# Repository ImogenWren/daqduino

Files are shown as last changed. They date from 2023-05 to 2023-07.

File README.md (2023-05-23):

# DAQduino
 DAQ Arduino, Voltage and Current Data Aquisition Unit.
 
 ## Goal 
 DAQduino is a standalone DAQ device capable of logging data from 
a few sources to a CSV file on an SD card, sending data in realtime
to a PC, and displaying the data for a particular sensor on a screen
 
 ## Using Arduino for Data Aquisition
 
 _There are several different methods that could be used for basic Data Aquisition tasks with just a few sensors that are easy to integrate with the Arduino Platform._
 
 1. Arduino streams serial data in CSV format. 
    - Use Putty/Kitty to record log
    - Python program to log to file
    - LabVIEW program to log to file

 2. Arduino streams data in JSON format.
    - Use Putty/Kitty and export data later
    - Python to log to file

3. Arduino waits for serial message to release data packet
    - Putty/Kitty to record log
    - LabVIEW for full DAQ implementation
    - Python for basic IO Interface - command line?
    - Python Desktop App

4. Full Integration between arduino and desktop software.

### Functions:
 - 10v, 12v and 24v outputs for sensor power
 - 0 - 10v analog input
 - 0 - 5v TTL IO
 - 4 - 20mA input
 - OLED Screen
 - Encoder Control
 - Basic Scaling

#### Stretch Goals:
 - 0 - 10 v output
 - 0 - 20 mA output

### Communications:
- Serial Data
- Labveiw Integration?

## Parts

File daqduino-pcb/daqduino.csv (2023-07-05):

# | Reference | Qty | Value | Footprint | DNP | JLCpart | RSpart | FarnellPart | supplier | Cost
1 | C1 | 1 | 470n | Capacitor_SMD:C_0805_2012Metric_Pad1.18x1.45mm_HandSolder
2 | C2, C3, C4 | 3 | 100n | 000_Capacitors_Immo:C_0805_2012_HandSolder_kawaii |  | C779975 |  |  |  | 0.02
3 | D1 | 1 | red | Diode_SMD:D_0805_2012Metric_Pad1.15x1.40mm_HandSolder
4 | D2 | 1 | yellow | Diode_SMD:D_0805_2012Metric_Pad1.15x1.40mm_HandSolder
5 | D3 | 1 | green | Diode_SMD:D_0805_2012Metric_Pad1.15x1.40mm_HandSolder
6 | D4 | 1 | blue | Diode_SMD:D_0805_2012Metric_Pad1.15x1.40mm_HandSolder
7 | EC1, EC2 | 2 | 100u | Capacitor_SMD:CP_Elec_10x10
8 | J1 | 1 | 24v Power Input | 000_Connectors_Immo:TerminalBlock_Altech_AK300-2_P5.00mm
9 | J2 | 1 | Sense Current TestPoint | 000_Connectors_Immo:TerminalBlock_Altech_AK300-2_P5.00mm
10 | J3 | 1 | Bias Voltage & Resistor Selection | 000_Pin_Headers_Immo:PinHeader_2x03_P2.54mm-alt-pin-no
11 | J4 | 1 | Sensor Voltage Selection | 000_Pin_Headers_Immo:PinHeader_2x03_P2.54mm-alt-pin-no
12 | J5 | 1 | 2 Wire Sensor (4-20mA) | 000_Connectors_Immo:TerminalBlock_Altech_AK300-2_P5.00mm
13 | J7 | 1 | Micro_SD_Card-molex | 000_Connectors_Immo:microSD_HC_Molex_104031-0811 |  |  |  | 2678573 | https://uk.farnell.com/molex/104031-0811/connector-micro-sd-8pos/dp/2678573
14 | R1 | 1 | 220r | Resistor_SMD:R_0805_2012Metric_Pad1.20x1.40mm_HandSolder
15 | R2, R3, R10 | 3 | 10k | Resistor_SMD:R_0805_2012Metric_Pad1.20x1.40mm_HandSolder |  | C2930231 |  |  |  | 0.002
16 | R4 | 1 | 100r | Resistor_SMD:R_0805_2012Metric_Pad1.20x1.40mm_HandSolder |  | C217766 |  |  |  | 0.0093
17 | R5, R6, R7, R8, R9 | 5 | 3k3 | Resistor_SMD:R_0805_2012Metric_Pad1.20x1.40mm_HandSolder
18 | R11 | 1 | 4k7 | Resistor_SMD:R_0805_2012Metric_Pad1.20x1.40mm_HandSolder |  | C2930231 |  |  |  | 0.002
19 | R12 | 1 | 2k2 | Resistor_SMD:R_0805_2012Metric_Pad1.20x1.40mm_HandSolder |  | C2930231 |  |  |  | 0.002
20 | R13 | 1 | 1k | Resistor_SMD:R_0805_2012Metric_Pad1.20x1.40mm_HandSolder |  | C2930231 |  |  |  | 0.002
21 | TP1 | 1 | 24v TestPoint | TestPoint:TestPoint_Bridge_Pitch2.54mm_Drill1.0mm
22 | TP2 | 1 | 12v TestPoint | TestPoint:TestPoint_Bridge_Pitch2.54mm_Drill1.0mm
23 | TP3 | 1 | 5v TestPoint | TestPoint:TestPoint_Bridge_Pitch2.54mm_Drill1.0mm
24 | TP4 | 1 | 3v3 TestPoint | TestPoint:TestPoint_Bridge_Pitch2.54mm_Drill1.0mm
25 | TP5 | 1 | Bias TestPoint | TestPoint:TestPoint_Bridge_Pitch2.54mm_Drill1.0mm
26 | TP6 | 1 | Sense Voltage TestPoint | TestPoint:TestPoint_Bridge_Pitch2.54mm_Drill1.0mm
27 | U1 | 1 | LM358 | Package_SO:SOIC-8_3.9x4.9mm_P1.27mm |  |  | 689-6719 |  | https://uk.rs-online.com/web/p/op-amps/6896719?gb=s
28 | U2 | 1 | L7812 | Package_TO_SOT_THT:TO-220-3_Vertical |  |  | 793-1355 |  | https://uk.rs-online.com/web/p/voltage-regulators/7931355?gb=s
29 | U3 | 1 | TXS0108EPW | Package_SO:TSSOP-20_4.4x6.5mm_P0.65mm |  |  | 709-4639 |  | https://uk.rs-online.com/web/p/translator-ics/7094639?gb=s
30 | XA1 | 1 | Arduino_Uno_R3_Shield | PCM_arduino-library:Arduino_Uno_R3_Shield |  |  | 769-7409 |  | https://uk.rs-online.com/web/p/arduino/7697409?gb=s

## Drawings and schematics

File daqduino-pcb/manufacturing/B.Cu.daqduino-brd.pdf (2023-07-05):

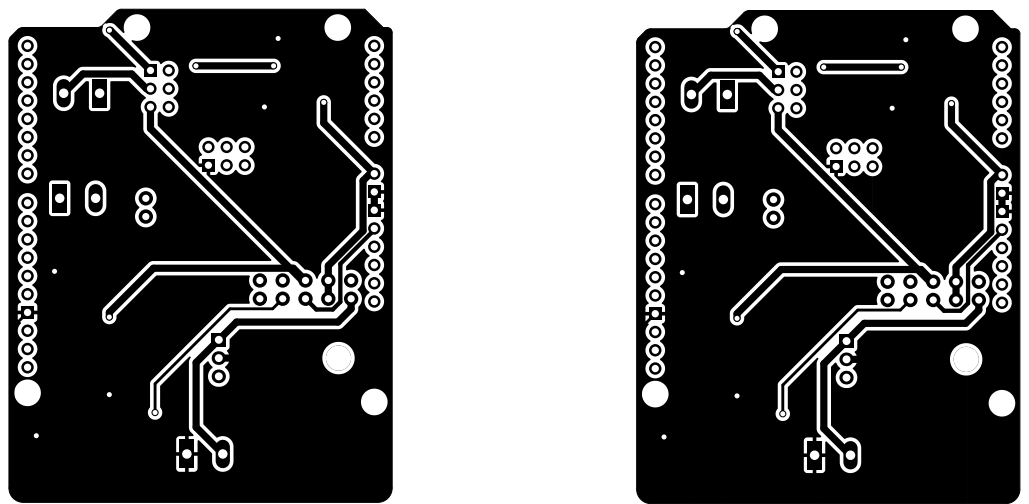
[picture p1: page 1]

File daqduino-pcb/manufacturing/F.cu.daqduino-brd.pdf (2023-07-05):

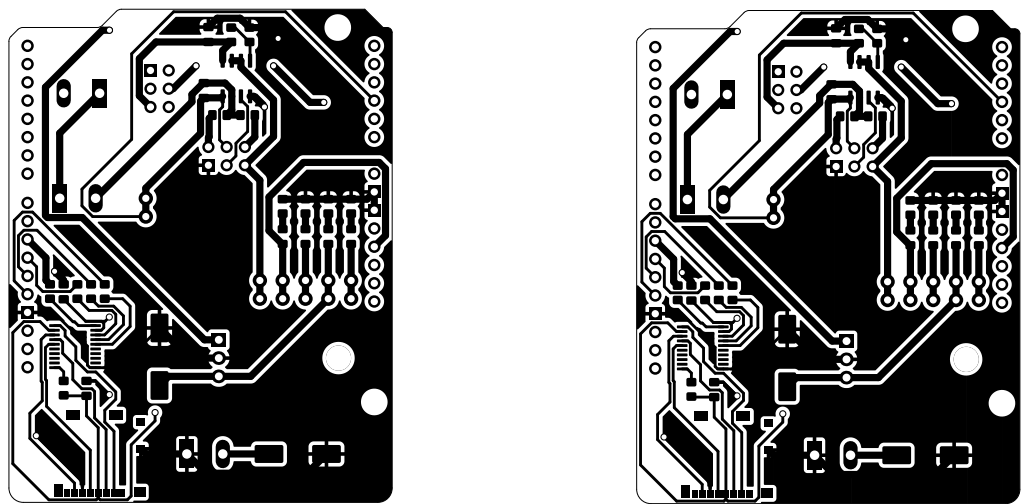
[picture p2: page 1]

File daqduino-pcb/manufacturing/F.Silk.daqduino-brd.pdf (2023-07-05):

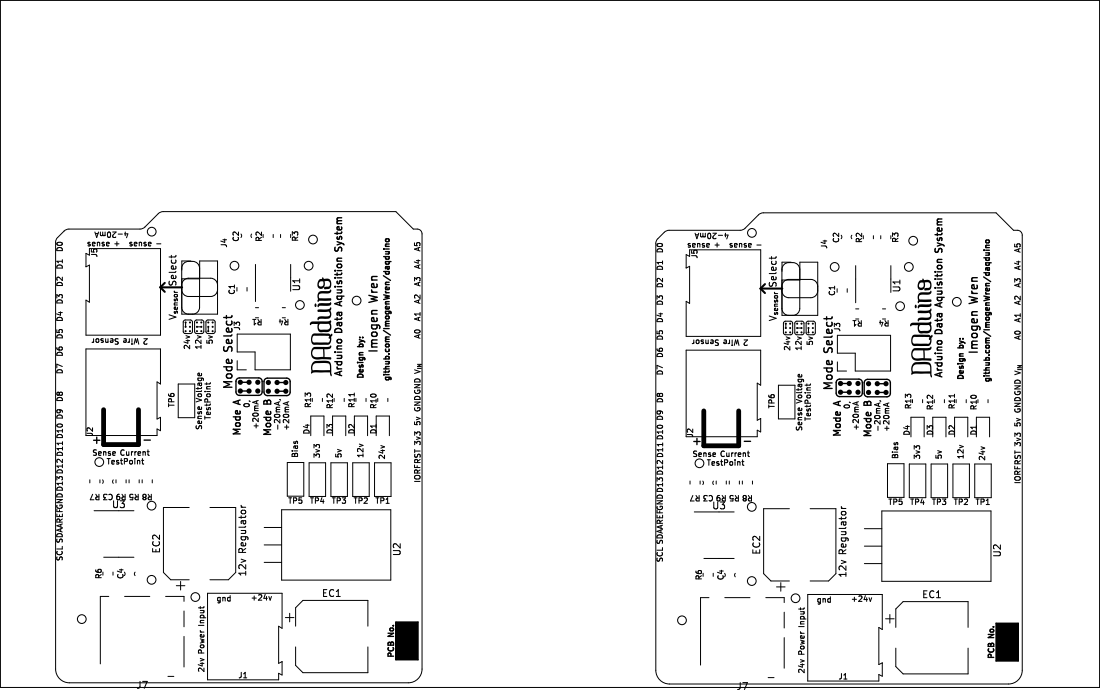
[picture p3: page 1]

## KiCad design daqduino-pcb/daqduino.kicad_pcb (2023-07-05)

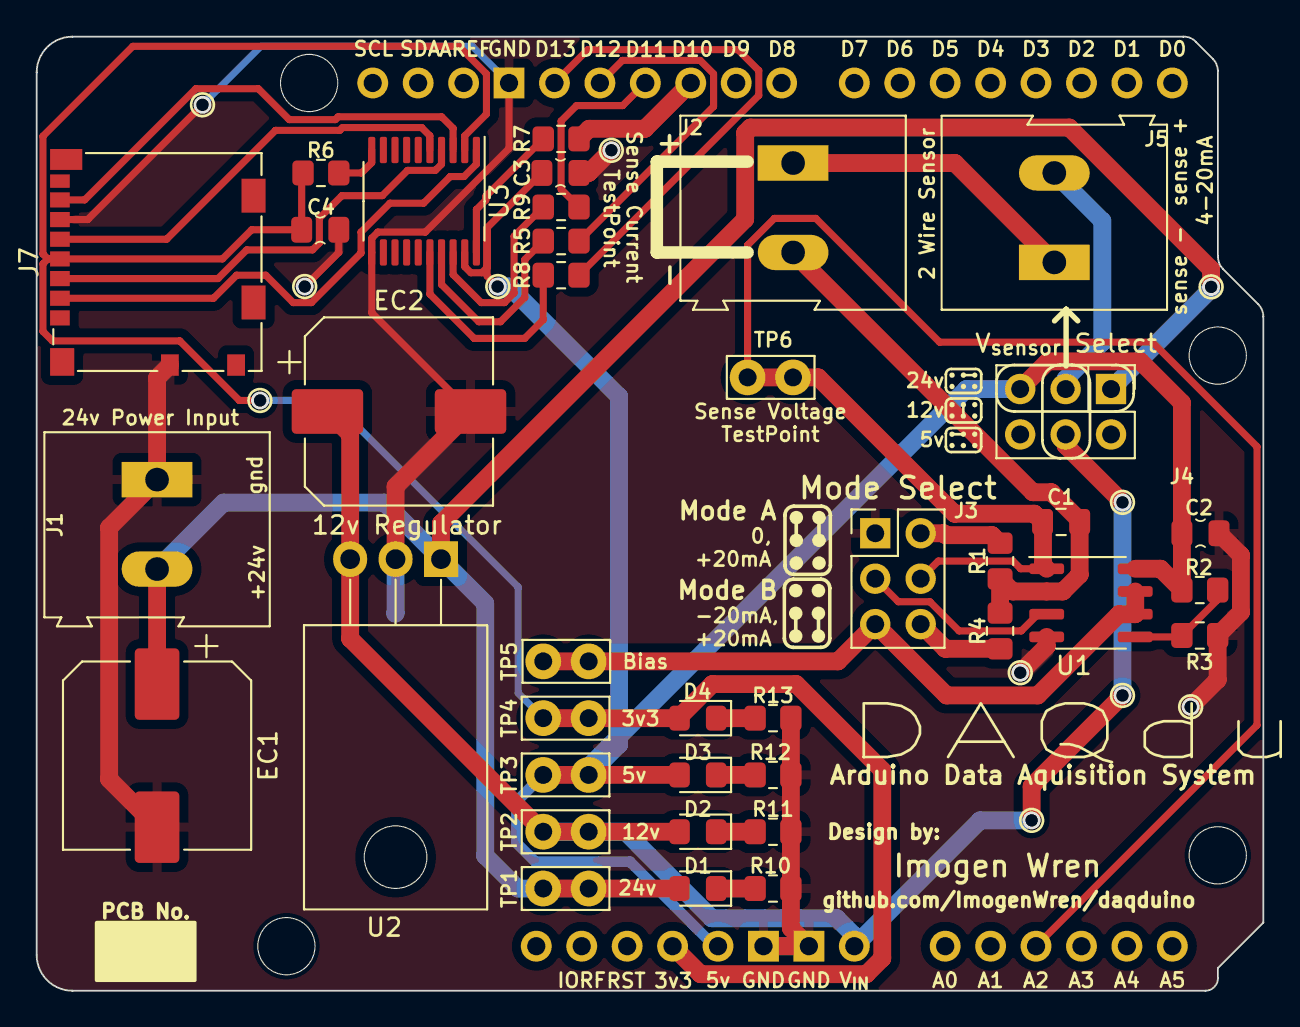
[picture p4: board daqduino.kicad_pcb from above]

Board: 2 copper layers, 68.6 x 53.3 mm, 39 parts (0 on the bottom side), 31 nets.

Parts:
C1: 470n; C_0805_2012Metric_Pad1.18x1.45mm_HandSolder
C2, C3, C4: 100n; C_0805_2012_HandSolder_kawaii
D1: red; D_0805_2012Metric_Pad1.15x1.40mm_HandSolder
D2: yellow; D_0805_2012Metric_Pad1.15x1.40mm_HandSolder
D3: green; D_0805_2012Metric_Pad1.15x1.40mm_HandSolder
D4: blue; D_0805_2012Metric_Pad1.15x1.40mm_HandSolder
EC1, EC2: 100u; CP_Elec_10x10
J1: 24v Power Input; TerminalBlock_Altech_AK300-2_P5.00mm
J2: Sense Current; TerminalBlock_Altech_AK300-2_P5.00mm
J3: Mode Select; PinHeader_2x03_P2.54mm-alt-pin-no
J4: V_{sensor} Select; PinHeader_2x03_P2.54mm-alt-pin-no
J5: 2 Wire Sensor; TerminalBlock_Altech_AK300-2_P5.00mm
J7: Micro SD Card; microSD_HC_Molex_104031-0811
R1: 220r; R_0805_2012Metric_Pad1.20x1.40mm_HandSolder
R2, R3, R10: 10k; R_0805_2012Metric_Pad1.20x1.40mm_HandSolder
R4: 100r; R_0805_2012Metric_Pad1.20x1.40mm_HandSolder
R5, R6, R7, R8, R9: 3k3; R_0805_2012Metric_Pad1.20x1.40mm_HandSolder
R11: 4k7; R_0805_2012Metric_Pad1.20x1.40mm_HandSolder
R12: 2k2; R_0805_2012Metric_Pad1.20x1.40mm_HandSolder
R13: 1k; R_0805_2012Metric_Pad1.20x1.40mm_HandSolder
TP1: 24v; TestPoint_Bridge_Pitch2.54mm_Drill1.0mm
TP2: 12v; TestPoint_Bridge_Pitch2.54mm_Drill1.0mm
TP3: 5v; TestPoint_Bridge_Pitch2.54mm_Drill1.0mm
TP4: 3v3; TestPoint_Bridge_Pitch2.54mm_Drill1.0mm
TP5: Bias; TestPoint_Bridge_Pitch2.54mm_Drill1.0mm
TP6: Sense Voltage; TestPoint_Bridge_Pitch2.54mm_Drill1.0mm
U1: LM358; SOIC-8_3.9x4.9mm_P1.27mm
U2: 12v Regulator; TO-220-3_Horizontal_TabDown
U3: TXS0108EPW; TSSOP-20_4.4x6.5mm_P0.65mm
XA1: Arduino_Uno_R3_Shield-simple

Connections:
/3V3_BUS: C4.1, D4.2 (A), J7.4 (VDD), R6.2, TP4.1, U3.2 (VCCA), XA1.3V3 (3.3V)
/5V_BUS: C2.1, C3.1, D3.2 (A), J4.3, R2.2, TP3.1, U1.8 (V+), U3.19 (VCCB), XA1.5V1 (5V)
/12V_BUS: D2.2 (A), EC2.1, J4.5, TP2.1, U2.3 (OUT), XA1.VIN
/24V_BUS: D1.2 (A), EC1.1, J1.2, J4.1, TP1.1, U2.1 (IN)
/BIAS_VOLTAGE: J3.2, U1.3 (+)
/CHIP_SELECT: R7.1, XA1.D10 (D10_CS)
/CLK: J7.5 (CLK), U3.5 (A4)
/CS: J7.2 (DAT3/CD), U3.1 (A1)
/D_{IN}: J7.3 (CMD), U3.4 (A3)
/D_{OUT}: J7.7 (DAT0), U3.3 (A2)
/MISO: R9.1, XA1.D11
/MOSI: R5.1, XA1.D12
/R_SET_A: C1.1, J2.2, R1.2, R4.2, U1.2 (-)
/R_SET_B: C1.2, J3.5, TP6.1, U1.1, XA1.A2
/SCK: R8.1, XA1.D13
/SENSE_CURRENT: J2.1, J5.1
/SENSOR_POWER: J4.2, J5.2
GND: C2.2, C3.2, C4.2, EC1.2, EC2.2, J1.1, J3.1, J7.6 (VSS), J7.9 (SHIELD), R3.1, R10.1, R11.1, R12.1, R13.1, U1.4 (V-), U2.2 (GND), U3.11 (GND), XA1.GND1 (GND), XA1.GND2 (GND), XA1.GND3 (GND)
unnamed: D1.1 (K), R10.2
unnamed: D2.1 (K), R11.2
unnamed: D3.1 (K), R12.2
unnamed: D4.1 (K), R13.2
unnamed: J3.3, TP5.1, U1.6 (-), U1.7
unnamed: J3.4, R4.1
unnamed: J3.6, R1.1
unnamed: R2.1, R3.2, U1.5 (+)
unnamed: R7.2, U3.20 (B1)
unnamed: R9.2, U3.18 (B2)
unnamed: R5.2, U3.17 (B3)
unnamed: R8.2, U3.16 (B4)
unnamed: R6.1, U3.10 (OE)

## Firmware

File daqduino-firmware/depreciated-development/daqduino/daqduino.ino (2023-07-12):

/*   DAQduino - Firmware - V0.1

          DAQduino is an open-source Data AQuisition (DAQ) Device
            designed to free researchers and students from
            the Tyranny of National Instruments and LabVIEW.

            It can be used as a standalone datalogger, saving data to an SD card for later,
            or it can be interfaced with a veriety of software to gather real-time data and 
            share this with other devices 

    This is Firmware Version 0.1. It will have reduced functionality while the system is being developed.

    Version 0.1
    Imogen Wren H.
    05/07/2023

*/


/*  Initial Scaling - Based on "theory" and "maths"

          Volts per ADC = 4.89 mV
                        = 0.00489 V

          DAQduino internal amplifier is set up for 

          20 mA ~= 4.4 V output

          Therefore:

          scale:

          mA = 20/4.4(Vmeasured)
          mA = 4.54(Vmeasured)
*/

/*  First Test

          To account for DC offset in readings, measure difference between multimeter readings and DAQduino reporting.
          To Start: 
|         | ADC   |  Vreported  | Vmeasured  | Vdiff    | % diff   | mA reported | mA measured  | mA diff |
|---      |---    |---          |---         |---       |---       |---          |---           |---      |
| Lowest  | 162   |   0.792     |   0.772    |  0.02    |          | 3.596       | 2.11         | 1.486   |
|MidRange | 400   |   1.956     |   1.888    |  0.068   |          | 8.880       | 20.69        |-11.81   |  
| Highest | 632   |   3.090     |   2.977    |  0.113   |          | 14.031      | 23.47        |-9.439   |
|---      |---    |---          |---         |---       |---       |---          |---           |         |


*/

/* Actual Scale - Defintion Based on Measurements

    - This method of calibration should work for any sensor with a linear output, as long as measured voltage is accurate, and the true value used in calibration is known
          - e.g. if a pressor sensor voltage can be tested at a specific known pressure.

Step 1: Record the detected voltage and the sensor true value for minimum and maximum possible datapoints.
Step 2: Calculate range, divisions and offset for each set of data.
Step 3: Place Values into algorithm as indicated
Step 4: ...?? Profit ?

    - Use the following table to assist

|                        | Voltage (V)  |Sensor True Value (measured)|       |
|---                     |---           |---                         |---    |
|Min                     |	 3.295      |	     2.06	                 |  mA	 |
|Max                     |  4.298	      |    	22.4	                 |  mA   |	
|Range (max - min)       |	 1.003      |     20.34                  |  mA   |
|ScaleFactor(Voltage/STV)|	 0.049		  |	     1.0                   | V/mA  |
|ScaleFactor(STV/Voltage)|	 1.0		    |     20.3                   | mA/v  |
|Offset                  |  3.295       |	     2.06                  |  mA   |	       	
					
      sensor_value = ((Vin - Voffset) * ScaleFactor(mA/V)) + mAoffset 			

*/

//#define ADC_VOLTS_SCALER 0.0048876  // Value Gained via maths for ADC scale calculation
//#define ADC_VOLTS_SCALER 0.0047341     // Value taking into account 3.14% average difference between top and bottom values
//#define ADC_VOLTS_SCALER 0.0045854     // wwinging it at this point (too low)
//#define ADC_VOLTS_SCALER 0.0046969       // still slightly too low
#define ADC_VOLTS_SCALER 0.0047339

#define mA_PER_VOLT 20.3
#define mA_OFFSET 2.06
#define V_OFFSET 3.295

/* Algorithm:

mA = (Vreading - V_OFFSET)* mA_PER_VOLT + mA_OFFSET

*/
#define VOLTAGE_SENSE_PIN A2
#define SD_SELECT_PIN 10


#define BENCHMARK_SAMPLING  // print benchmark testing output for sampling function
//#define BENCHMARK_LOOP      // print benchmark testing output for entire program loop  // use to check sample rate targets met
//#define PRINT_RAW_DATA     // Print all raw ADC samples before averaging (for debugging purposes)
#define SERIAL_PRINT_TRUE  // Print data output to serial monitor (comment out for faster sampling)?
#define LOG_TO_SD_CARD     // Log data to SD card

//#define USE_SDFAT_LIB  // User option to use SD FAT library instead of standard one (untested)
// If undefined then typical arduino library is used.

#include "sd-functions.h"


bool cardAvailable = false;  // must start true then will be made false if SD Cannot be found


void SDcardSetup() {
  pinMode(SD_SELECT_PIN, OUTPUT);
  Serial.print("\nInitializing SD card...");
  int attempt;
  // we'll use the initialization code from the utility libraries
  while (attempt < 10) {
#ifdef USE_SDFAT_LIB
    if (!card.init(SPI_HALF_SPEED, SD_SELECT_PIN))
#else
    if (!SD.begin(SD_SELECT_PIN))
#endif
    {
      Serial.print("Attempt: ");
      Serial.print(attempt);
      Serial.println("\n\ninitialization failed. Is SD card present?");
      delay(400);
      attempt++;
    } else {
      Serial.println("Wiring is correct and a card is present.");
      cardAvailable = true;
    }
  }
  if (!cardAvailable) {
    Serial.println("Too Many Attempts - SD Logging disabled");
  }
}



// Function to take multiple samples of ADC and return average of all samples
int sampleAverage(int no_samples = 100) {
  uint32_t startTime = millis();  // Take start Time for Benchmarking

  // Take samples
  int dataArray[no_samples];
  for (int i = 0; i < no_samples; i++) {
    dataArray[i] = analogRead(VOLTAGE_SENSE_PIN);
  }
  int samplesTaken = sizeof(dataArray) / sizeof(dataArray[0]);  // Divide the size of the whole array by the size of 1 index to = the number of indexes



#ifdef BENCHMARK_SAMPLING
#pragma message "Sampling Benchmarking Active"
  // For Benchmarking
  uint32_t finishTime = millis();
  uint32_t benchTime = finishTime - startTime;
  Serial.print(samplesTaken);
  Serial.print(" Samples Taken in: ");
  Serial.print(benchTime);
  Serial.print(" mS");
  Serial.println();
#endif

#ifdef PRINT_RAW_DATA
#pragma message "Raw Data Output Enabled"
  for (int i = 0; i < no_samples; i++) {
    Serial.print(i);
    Serial.print("  ADC: ");
    Serial.println(dataArray[i]);
  }
#endif

  float average = 0;
  // Do averaging
  for (int i = 0; i < no_samples; i++) {
    average = average + dataArray[i];
  }
  average = average / no_samples;  // change this to use sizeof array
  int32_t int_av = round(average);
  return int_av;
}



void printData(int adc_value, float V_float, float mA_float) {
  char buffer[64];  // Buffer to hold printed values
    // Strings for converting floats for printing
  char V_str[16];
  char mA_str[16];
  // Convert floats to string as arduino does not like floats in sprintf
  dtostrf(V_float, 4, 3, V_str);
  dtostrf(mA_float, 4, 3, mA_str);
  // Place all data into a single buffer & format for printing
  sprintf(buffer, "ADC: %4i  |  V: %s  |  mA: %s ", adc_value, V_str, mA_str);
  // Print the buffer
  Serial.println(buffer);
}


void setup() {
  Serial.begin(115200);
  Serial.println("\n DAQduino - Data AQuisition System");
  //analogReference(INTERNAL); // Only used for analog voltage sampling <1
  SDcardSetup();
}



void loop() {


  // int adc_value = analogRead(VOLTAGE_SENSE_PIN);  // Take single ADC Reading
  int adc_value = sampleAverage();  // Take 100 or (n) samples & average

  float V_float = float(adc_value) * ADC_VOLTS_SCALER;                // Calculate mV measured by ADC
  float mA_float = ((V_float - V_OFFSET) * mA_PER_VOLT) + mA_OFFSET;  // Calculate mA detected by op-amp


  printData(adc_value, V_float, mA_float);  // print data to serial monitor



  // Delay to slow down reporting for human readability
  delay(485);  //TODO: Replace this with a proper timer and sample rate conversion that can be checked via benchmarking
  // Strech function - warn user if true samplerate does not match their selection

#ifdef BENCHMARK_LOOP
#pragma message "Loop Benchmarking Active"
#endif
}

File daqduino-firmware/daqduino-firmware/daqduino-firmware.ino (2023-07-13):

/*  DAQduino - Firmware - V1.0

          DAQduino is an open-source Data AQuisition (DAQ) Device
            designed to free researchers and students from
            the Tyranny of National Instruments and LabVIEW.

            It can be used as a standalone datalogger, saving data in CSV format to an SD card for later,
            or it can be interfaced with a veriety of software to gather real-time data and 
            share this with other devices 

    This is Firmware Version 1.0(beta).
        - Basic functionality is complete, however may have unknown bugs.
        - More functionality will be realised in later versions.

    Version 1.0
    Imogen Wren H.
    12/07/2023

  # Notes on SD Card Logging Functionality:
      Each time the arduino reboots it will start a new log with a new number. It should be able to detect the number of the last log created so it will always pick the next highest Number.
      there may be edge cases where this does not work!

      Number of logs limited to 64 by a static array in sdFunctions. Increase the size of the array to allow more logs, but given the nature of SD cards, and their limited lifespan, it
      would be best to copy logs into a safe place and delete them from SD card before it is likely to hit this limit to avoid data loss!

      Formatting SD Card:
          - Use FAT32


*/

/*
  ## First Use Instructions:
    - Plug in formatted SD Card.
    - Reboot Unit
    - Ensure that new log file is being created.
    - Power down unit
    - Check SD for useable data
    - Delete unused logs
    - Start Data AQuisition
*/

/* # DAQduino - Maths and Scaling
Initial Scaling - Based on "theory" and "maths"

          Volts per ADC = 4.89 mV
                        = 0.00489 V

          DAQduino internal amplifier is set up for 
          20 mA ~= 4.4 V output

          Therefore:
          scale:
          mA = 20/4.4(Vmeasured)
          mA = 4.54(Vmeasured)


##  First Test

          To account for DC offset in readings, measure difference between multimeter readings and DAQduino reporting.
          To Start: 
|         | ADC   |  Vreported  | Vmeasured  | Vdiff    | % diff   | mA reported | mA measured  | mA diff |
|---      |---    |---          |---         |---       |---       |---          |---           |---      |
| Lowest  | 162   |   0.792     |   0.772    |  0.02    |          | 3.596       | 2.11         | 1.486   |
|MidRange | 400   |   1.956     |   1.888    |  0.068   |          | 8.880       | 20.69        |-11.81   |  
| Highest | 632   |   3.090     |   2.977    |  0.113   |          | 14.031      | 23.47        |-9.439   |
|---      |---    |---          |---         |---       |---       |---          |---           |         |




## Actual Scale - Defintion Based on Measurements

    - This method of calibration should work for any sensor with a linear output, as long as measured voltage is accurate, and the true value used in calibration is known
          - e.g. if a pressor sensor voltage can be tested at a specific known pressure.

Step 1: Record the detected voltage and the sensor true value for minimum and maximum possible datapoints.
Step 2: Calculate range, divisions and offset for each set of data.
Step 3: Place Values into algorithm as indicated
Step 4: ...?? Profit ?

    - Use the following table to assist

|                        | Voltage (V)  |Sensor True Value (measured)|       |
|---                     |---           |---                         |---    |
|Min                     |	 3.295      |	     2.06	                 |  mA	 |
|Max                     |   4.298      |    	22.4	                 |  mA   |	
|Range (max - min)       |	 1.003      |     20.34                  |  mA   |
|ScaleFactor(Voltage/STV)|	 0.049		  |	     1.0                   | V/mA  |
|ScaleFactor(STV/Voltage)|	 1.0		    |     20.3                   | mA/v  |
|Offset                  |   3.295      |	     2.06                  |  mA   |	       	
					
      sensor_value = ((Vin - Voffset) * ScaleFactor(mA/V)) + mAoffset 			

*/

#pragma message "See globals.h for user configuration options"

// Nessissary Include Statements
#include <SPI.h>
#include <SD.h>
#include "globals.h"
#include "timeFunctions.h"
#include "sdFunctions.h"
#include "dataFunctions.h"


// All values required for translation of ADC values to actual sensor values
// Values found through mix of "theory" and experimentation
//#define ADC_VOLTS_SCALER 0.0048876  // Value Gained via maths for ADC scale calculation
//#define ADC_VOLTS_SCALER 0.0047341     // Value taking into account 3.14% average difference between top and bottom values
//#define ADC_VOLTS_SCALER 0.0045854     // wwinging it at this point (too low)
//#define ADC_VOLTS_SCALER 0.0046969       // still slightly too low
#define ADC_VOLTS_SCALER 0.0047339

#define mA_PER_VOLT 20.3
#define mA_OFFSET 2.06
#define V_OFFSET 3.295

/* Algorithm for Voltage to mA:

mA = (Vreading - V_OFFSET)* mA_PER_VOLT + mA_OFFSET

*/




// Structure is useful if more than 1 data point is being collected/processed as each data type can be added to structure without changing functions too much based on data types and amounts used!
// Define all data which should be logged/printed in this structure
struct dataStruct {
  float dataA;  // in this case will be voltage
  float dataB;  // In this case will be mA
};

dataStruct globalData;  // Create a global instance to share between functions easily

// Edit this function to change data headers
void logDataHeader() {
  char buffer[32];
  char entryNo[8] = { "Entry" };
  char timeStamp[10] = { "Timestamp" };
  char dataHeadingA[8] = { "Voltage" };
  char dataHeadingB[8] = { "mA" };
  sprintf(buffer, "%s, %s, %s, %s, \n", entryNo, timeStamp, dataHeadingA, dataHeadingB);  // make sure to include "\n for newline"
  Serial.println(buffer);
  log_to_SD(buffer);
}



// Edit this function to change what/how data is aquired and processed
void sampleData() {
  // int adc_value = analogRead(VOLTAGE_SENSE_PIN);  // Take single ADC Reading
  int adc_value = sampleAverage();  // Take 100 or (n) samples & average

  float V_float = float(adc_value) * ADC_VOLTS_SCALER;                // Calculate mV measured by ADC
  float mA_float = ((V_float - V_OFFSET) * mA_PER_VOLT) + mA_OFFSET;  // Calculate mA detected by op-amp

  globalData = { V_float, mA_float };  // This could be returned locally but for simplicity global variable is used
}
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

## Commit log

2023-05-23 Started work on desktop app using python
    [daqduino.kicad_pcb, daqduino.kicad_sch]
2023-06-05 almost finished schematic
    [daqduino.kicad_sch]
2023-06-07 started pcb laypouty
    [daqduino.kicad_pcb, daqduino.kicad_sch]
2023-06-08 finished PCB design
    [daqduino.kicad_pcb, daqduino.kicad_sch]
